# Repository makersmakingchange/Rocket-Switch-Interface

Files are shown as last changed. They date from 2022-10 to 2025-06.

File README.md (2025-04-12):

# Rocket Switch Interface
The Rocket Switch Interface is a switch interface device which enables users to operate their computer or smartphone devices using assistive switches. The Rocket Switch Interface supports up to two 3.5 mm assistive switches as input.

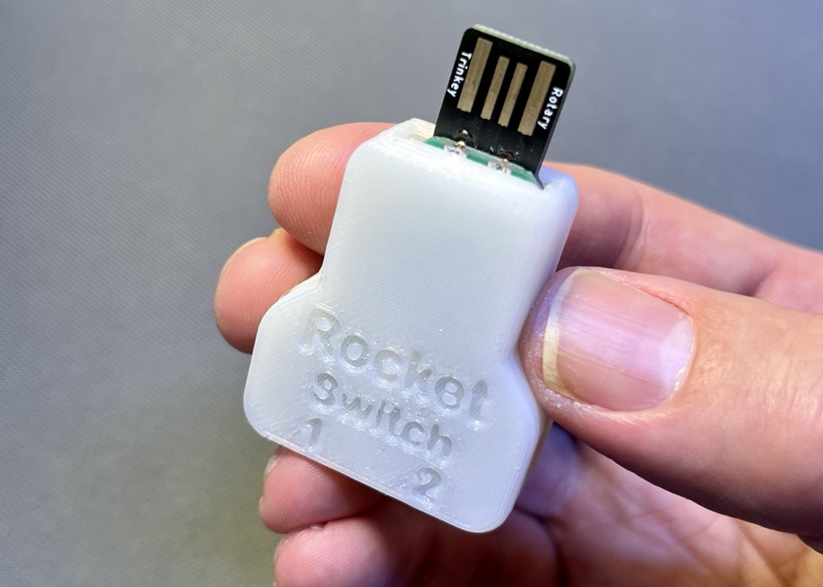
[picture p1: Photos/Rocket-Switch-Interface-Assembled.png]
A picture of a 3d printed Rocket Switch Interface


## More info at
- [Makers Making Change Project Page](https://makersmakingchange.com/project/rocket-switch-interface/)

## Usage
Both switches can be used as inputs when short pressed, Switch 1 can be used to change the operation mode when it's pressed and hold for 4 seconds. The device can operate in several modes:

 - Switch Mac Mode: This mode can be used along switch control software available for Windows, Android, iOS, and Mac Operating Systems. Switch 1 outputs the Space key and switch 2 outputs the Enter key.

 - Switch Mode: This mode can be used along switch control software available for Windows, Android, and iOS Operating Systems. Switch 1 outputs the 1 key and switch 2 outputs the 2 key.

 - Mouse Mode: This mode can be used to simulate a mouse button click. Switch 1 performs left mouse click and switch 2 performs right mouse click.

 - Settings Mode: The settings mode allows the user to adjust the reaction time between switch presses. There are 10 levels in total and the default reaction level is set to 9. The minimum reaction time is 50ms ( Level 10 ) and maximum reaction time is 500ms ( Level 1 ). Switch 1 decrements the reaction level by 1 level and switch 2 increments the reaction level by 1 level as well.

## How to Obtain a Rocket Switch Interface

### 1. Do it Yourself (DIY) or Do it Together (DIT)

This is an open-source assistive technology, so anyone is free to build it. All of the files and instructions required to build the device are contained within this repository. Refer to the Maker Checklist below.

### 2. Request a build of this device

If you would like to obtain this device, you may submit a build request through the [MMC Library Page](https://makersmakingchange.com/project/rocket-switch-interface/). The requestor is responsible for the cost of materials and any shipping.

### 3. How to build this device for someone else

If you have the skills and equipment to build this device, and would like to donate your time to create the switch for someone who needs it, visit the [MMC Maker Wanted](https://makersmakingchange.com/maker-wanted/) section.

## Getting Started

### 1. Read the Makers Checklist

The Makers Checklist provides an overview of the steps required to build this device.

### 2. Order the Off-The-Shelf Components

The [Bill of Materials](/Documentation/Rocket_Switch_Interface_BOM.xlsx) lists all of the parts and components required to build the Rocket Switch Interface.

### 3. Print the 3D Printable components

All of the files and individual print files can be in the [/Build_Files/3D_Printing_Files](/Build_Files/3D_Printing/) folder.

### 4. Assemble the Device

Reference the [Assembly Guide](/Documentation/Rocket_Switch_Interface_Assembly_Guide.pdf) for the tools and steps required to build each portion.

## Files
### Documentation
| Document             | Version | Link |
|----------------------|---------|------|
| Design Rationale     | 1.1     | [Rocket Switch Interface Design_Rationale](/Documentation/Rocket_Switch_Interface_Design_Rationale.pdf)     |
| Maker Checklist      | 1.1     | [Rocket Switch Interface Link_Maker_Checklist](/Documentation/Rocket_Switch_Interface_Maker_Checklist.pdf)     |
| Bill of Materials    | 1.1     | [Rocket Switch Interface Link_Bill_of_Materials](/Documentation/Rocket_Switch_Interface_BOM.xlsx)     |
| 3D Printing Guide    | 1.1     | [Rocket Switch Interface Link_3D_Printing_Guide](/Documentation/Rocket_Switch_Interface_3D_Printing_Guide.pdf)     |
| Assembly Guide       | 1.1     | [Rocket Switch Interface Link_Assembly_Guide](/Documentation/Rocket_Switch_Interface_Assembly_Guide.pdf)     |
| User Guide           | 1.1     | [Rocket Switch Interface Link_User_Guide](/Documentation/Rocket_Switch_Interface_User_Guide.pdf)    |
| Changelog            | 1.1     | [Rocket Switch Interface Link_Changelog](/Documentation/Rocket_Switch_Interface_Changelog.pdf)     |

### Design Files
 - [CAD Files](/Design_Files)

### Build Files
 - [3D Printing Files](/Build_Files/3D_Printing_Files)

## Attribution
Designers:
 - Milad Hajihassan, Makers Making Change

Contributors:
 - Derrick Andrews, Makers Making Change

## License
Everything needed or used to design, make, test, or prepare the Rocket Switch Interface Link is licensed under the CERN 2.0 Weakly Reciprocal license <https://ohwr.org/project/cernohl/wikis/Documents/CERN-OHL-version-2> (CERN-OHL-W) . 

Accompanying material such as instruction manuals, videos, and other copyrightable works that are useful but not necessary to design, make, test, or prepare the Rocket Switch Interface are published under a Creative Commons Attribution-ShareAlike 4.0 license https://creativecommons.org/licenses/by-sa/4.0/ (CC BY-SA 4.0).

----

<!-- ABOUT MMC START -->
## About Makers Making Change
[Makers Making Change Logo](https://www.makersmakingchange.com/)

Makers Making Change is a program of [Neil Squire](https://www.neilsquire.ca/), a Canadian non-profit that uses technology, knowledge, and passion to empower people with disabilities.

Makers Making Change leverages the capacity of community based Makers, Disability Professionals and Volunteers to develop and deliver affordable Open Source Assistive Technologies.

 - Website: [www.MakersMakingChange.com](https://www.makersmakingchange.com/)
 - GitHub: [makersmakingchange](https://github.com/makersmakingchange)
 - Bluesky: [@makersmakingchange.bsky.social](https://bsky.app/profile/makersmakingchange.bsky.social)
 - Instagram: [@makersmakingchange](https://www.instagram.com/makersmakingchange)
 - Facebook: [makersmakechange](https://www.facebook.com/makersmakechange)
 - LinkedIn: [Neil Squire Society](https://www.linkedin.com/company/neil-squire-society/)
 - Thingiverse: [makersmakingchange](https://www.thingiverse.com/makersmakingchange/about)
 - Printables: [MakersMakingChange](https://www.printables.com/@MakersMakingChange)

### Contact Us
For technical questions, to get involved, or to share your experience we encourage you to [visit our website](https://www.makersmakingchange.com/) or [contact us](https://www.makersmakingchange.com/s/contact).
<!-- ABOUT MMC END -->

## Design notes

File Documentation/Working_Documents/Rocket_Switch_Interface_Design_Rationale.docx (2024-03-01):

# Introduction

The goal is to create a low-cost switch interface that can be alternative to commercial options. The device needs be able to perform the main functions that is offered in alternative devices.

# Research

Commercial Alternatives

Device | Company | Inputs | Information | Cost ($US)
Swifty (https://orin.com/access/swifty/) | Origin Instruments | - 2 - Stereo Jack (Requires splitter) | - Splitter is sold separately: $10 - USB Extension: $10 | $99
Tapio (https://www.orin.com/access/tapio/) | Origin Instruments | - 2 - Stereo Jack (Requires splitter) | - iPad and iPhone Switch Interface | $120
Tecla Shield (https://www.iaccessibility.com/accessories/switches/index.cgi/product?ID=41) | Tecla | - 2 mono jacks + 4 way Joystick d-pad | - Discontinued? - 9-pin DB connection for joysticks
Hitch 2 (https://www.especialneeds.com/shop/assistive-technology/switches/switch-interfaces/hitch-2.html) | Ablenet | - 4 | - Ability to program one to four keystrokes of your choice - 9-pin DB connection for joysticks | $120
JoyCable (https://thinksmartbox.com/product/joycable/) | Thinksmartbox | - 2 | - Up to 2 switches (https://thinksmartbox.com/wp-content/uploads/2016/07/JoyCable-manual-July-2016-web-2.pdf) | £99.00 or $118
Crick USB Switch Box (https://www.cricksoft.com/us/crick-usb-switch-box) | Crick Software Inc. | - 4 | - Works on Windows and Mac computers - Crick Software application | $160

DIY Alternatives

Device | Creator | Inputs | Information | Cost ($US)
Enabled Controller Mini (https://makersmakingchange.com/project/enabled-controller-mini/) | Milador | - 4 input jacks and 2-axis analog input | - Morse code mode - Morse mouse mode - Gaming firmware | $40
ATMakers KeySwitch (https://makersmakingchange.com/project/keyswitch/) | ATMakers | - 5 | - Low memory issue with the selected MCU - Gaming firmware | $40
FAIO Multiplexer (https://makersmakingchange.com/project/faio-multiplexer/) | Milador | - 4 | - Morse code mode - Morse mouse mode - Gaming firmware | $55

# Requirements

## Goals

ID | Description
G01 | Cost Effective (Low cost comparing to alternative options)
G02 | Easy to use
G03 | Easy to assemble
G04 | Minimal size

## Functional Requirements

ID | Description
F01 | The device shall have one or more input channels.
F02 | The device shall send output data via USB HID to the host device.
F03 | The device shall be compatible with switch control software.
F04 | The device switch shall incorporate minimal input protection.
F05 | The device latency shall not exceed 50 milliseconds.
F06 | The device shall support visual feedback for user interactions.
F07 | The device shall not consume more than 20 mA of current from the USB port.
F08 | The device shall be able to perform Mouse button, joystick button and keyboard emulation.
F09 | The device shall weigh less than 25 grams.
F10 | The device shall be smaller than 50mm x 40mm x 20mm.

## Non-functional Requirement

ID | Description
NF01 | Shall look professional with tight tolerance on case size.
NF02 | Input ports should be legibly labelled for easy identification

## Constraints

ID | Description
C01 | Shall be able to be built as a single unit for ≤ $40 CAD
C02 | Shall be easily manufacturable by a moderately skilled maker

# Ideation

The initial idea was to add a custom PCB to an existing, small-sized commercially available microcontroller board.

There are a few other ways this could be accomplished:

- Using components with a proto board and breadboard-friendly 3.5 mm jacks
- Using components in a 3D printed jig / 3d printed PCB
- Using panel mount switch jacks mounted in a 3d printed enclosure

## Production Options

Simple maker manufacturing

a. Custom PCB
b. 3D printed case
c. Thru-hole soldering
d. Programming through open-source software

# Conceptual Design

## Components

### Dev Board/MCU

The TRINKEY board is a great low-cost option to design the switch interface based of it, as it offers the basic requirement for creation of a switch interface. Trinkey offer one to three GPIO’s and a built-in RGB LED in a small footprint (USB Flash Stick size).

The Trinkey is offered in following versions:

1. Adafruit NeoKey Trinkey (https://www.adafruit.com/product/5020)
      - Digikey Link: https://www.digikey.ca/en/products/detail/adafruit-industries-llc/5020/14307382
      - Cost: $10 CAD
      - Pros:
        - USB NeoPixel Mechanical Key Switch
        - LED Visible from top and bottom
        - One Touch pad
        - Factory code is compatible with Switch control on Android
      - Cons:
        - One GPIO
        - No exposed ground pad (Needs to use pull down)
2. Adafruit Rotary Trinkey (https://www.adafruit.com/product/4964)
      - DigiKey Link: https://www.digikey.ca/en/products/detail/adafruit-industries-llc/4964/14307384
      - Cost: $10
      - Pros:
        - 2 Analog pins and 1 digital pin exposed which can be used as three GPIO’s
        - One Touch pad
        - Power and ground pads exposed
      - Cons:
        - Factory code is not compatible with switch control software
        - LED Visible from bottom side
3. Adafruit Proximity Trinkey (https://www.adafruit.com/product/5022)
      - Digikey Link: https://www.digikey.ca/en/products/detail/adafruit-industries-llc/5022/15222465
      - Cost: $14 CAD
      - Pros:
        - Two Touch pads
        - Two RGB LEDs on top side
      - Cons:
        - Factory code is not compatible with switch control software
        - No Exposed GPIO’s
        - No exposed power and ground pad

This is not a suitable option because there are no solder pads readily accessible to connect a switch easily.

Both the Adafruit NeoKey Trinkey and the Adafruit Rotary Trinkey could be used to create a switch interface. The Adafruit Rotary Trinkey was selected for the following reasons:

1. Ability to use 2 switches
2. Ground pad is exposed.
3. The rotary switch has thru hole connections that make it easier to connect the switch jacks.

### 3.5 mm Input Jack Options

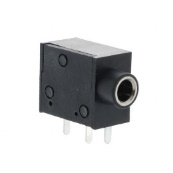
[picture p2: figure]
SJ1-3533NG
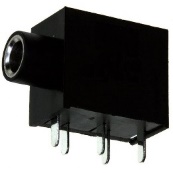
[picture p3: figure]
SJ1-3535NG
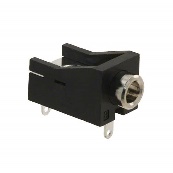
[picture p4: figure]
MJ-3536N
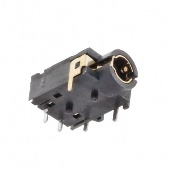
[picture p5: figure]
SJ-43514
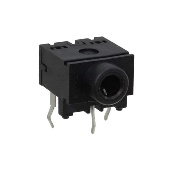
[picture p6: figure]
STX-3120-3B

3.5 mm Jack | SJ1-3533NG | SJ1-3535NG | MJ-3536N | SJ-43514 | STX-3120-3B
Type | Stereo (3 Conductor, TRS) | Stereo (3 Conductor, TRS) | Mono | Stereo (4 Conductor, TRRS) | Stereo (3 Conductor, TRS)
Cost (CAD$) | 1.9 to 1.92 | 1.93 to 1.96 | 1.37 to 1.39 | 1.45 to 1.47 | 1.15 to 1.16
Availability | 689,251 from Digikey, 21,251 from Mouser | 109,033 from Digikey, 5,468 from Mouser | 22,746 from Digikey, 8,534 from Mouser | 28,000 from Digikey, 27,750 from Mouser | 4,467 from Digikey, 5,220 from Mouser
Manufacturer | CUI Devices | CUI Devices | CUI Devices | CUI Devices | Kycon, Inc.
Dimensions | 14(+4) mm x 8.2mm x 12.3mm | 14(+4) mm x 8.2mm x 12.3mm | 15.8(+3) mm x 10mm x 10mm | 11(+3) mm x 4.9mm x 5mm | 10.5(+3.5) mm x 12mm x 10mm
Number of Sets | 1 | 1 | 1 | 1 | 1
Number of Positions | 3 Conductors, 3 Contacts | 3 Conductors, 5 Contacts | 2 Conductors, 3 Contacts | 4 Conductors, 4 Contacts | 3 Conductors, 3 Contacts
Voltage - Rated | 12VDC | 16VDC | 12VDC | 12VDC | N/A
Current Rating | 1A | 1A | 1A | 1A | N/A
Internal Switch | None | 2 Switches | Single Switch | None | None
ProtoBoard Friendly | No | No | No | No | Yes

Trinkey doesn’t provide enough pins to support jack internal switch (touch pad may not be a reliable method to provide additional input)

SJ-43514 is a reliable and low-cost option.

### Hardware pullup

Hardware pullup can be added as an optional feature

### Mounting Hole

A single M3 mounting hole to provide additional support for the enclosure.

## Concepts

### Concept 1: Mono

- Adafruit NeoKey Trinkey (https://www.adafruit.com/product/5020)
- One switch input through pull-down resistor
- Factory code can be used
- Total cost without PCB: $11.36
- Adafruit NeoKey Trinkey x 1: $9.73
- SJ-43514 3.5mm Jack Stereo x 1: $1.48
- 4.7 kΩ 1/4W Through Hole Resistor x 1: $0.15

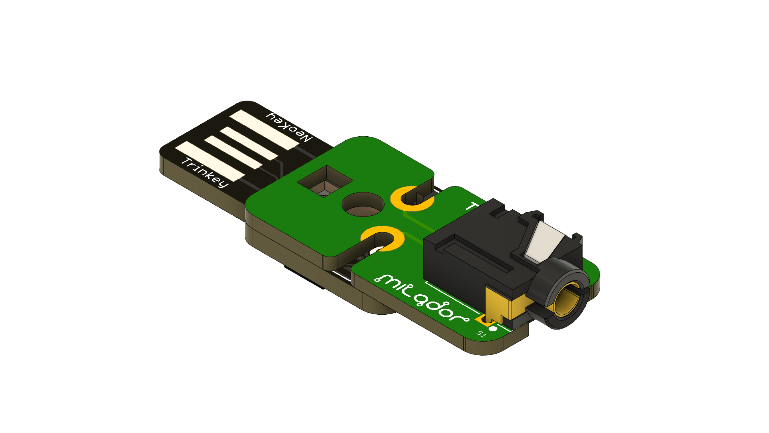
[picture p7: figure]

### Concept 2: Dual version 1

- Adafruit Rotary Trinkey (https://www.adafruit.com/product/4964)
- Two switch inputs through software/hardware pull-up resistor
- Low-cost option
- Total cost without PCB: $12.99
1) Adafruit Rotary Trinkey x 1: $9.73
2) SJ-43514 3.5mm Jack Stereo x 2: $1.48
3) 4.7 kΩ 1/4W Through Hole Resistor x 2: $0.15

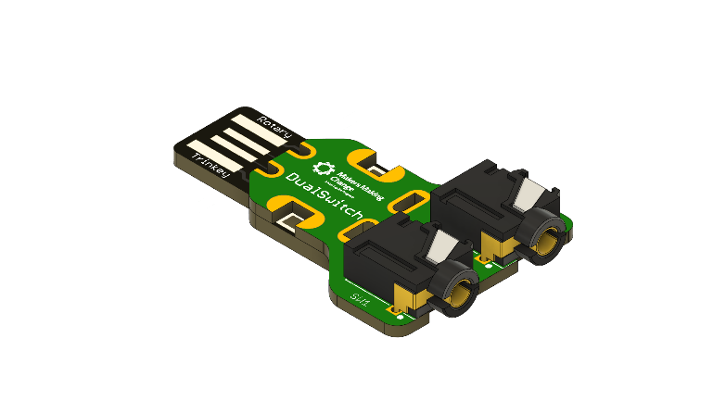
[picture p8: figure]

### Concept 3: Dual Version 2

- Adafruit Rotary Trinkey (https://www.adafruit.com/product/4964)
- Two vertical switch inputs (Jack with 2 sets) through software pull-down resistor
- Total cost without PCB: $14.47
4) Adafruit Rotary Trinkey x 1: $9.73
5) SJ-43514 3.5mm Jack Stereo x 1: $4.44
6) 4.7 kΩ 1/4W Through Hole Resistor x 2: $0.15

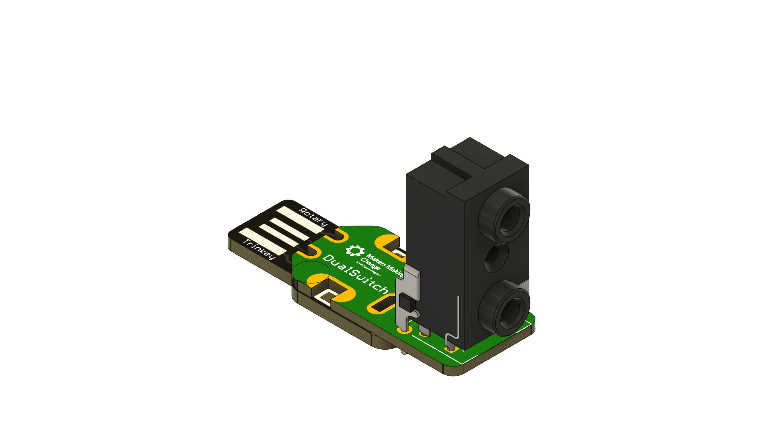
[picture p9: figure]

### Concept 4: Dual Version 3

- Adafruit NeoKey Trinkey (https://www.adafruit.com/product/5020)
- Two switch inputs through software/hardware pull-up resistor
- Total cost without PCB: $12.99
1) Adafruit NeoKey Trinkey x 1: $9.73
2) SJ-43514 3.5mm Jack Stereo x 2: $1.48
3) 4.7 kΩ 1/4W Through Hole Resistor x 2: $0.15

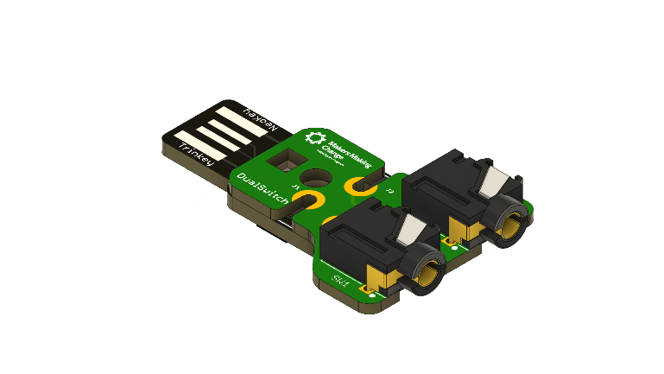
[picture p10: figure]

### Concept 5: Triple

- Adafruit Rotary Trinkey (https://www.adafruit.com/product/4964)
- Three vertical switch inputs (Jack with 3 sets) through software pull-up resistor
- Total cost without PCB: $14.85
4) Adafruit NeoKey Trinkey x 1: $9.73
5) SJ-43514 3.5mm Jack Stereo x 1: $4.67
6) 4.7 kΩs 1/4W Through Hole Resistor x 3: $0.15

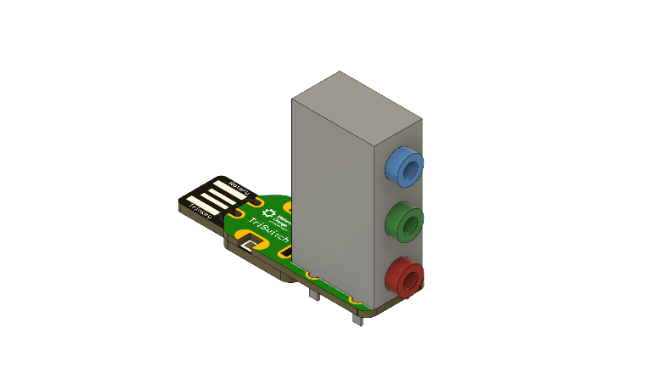
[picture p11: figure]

### Concept 6: Breadboard

- Adafruit Rotary Trinkey (https://www.adafruit.com/product/4964)
- SparkFun ProtoBoard
- Two breadboard friendly 3.5mm switch inputs through software pull-up resistor
- Total cost: $16.13
1) Adafruit NeoKey Trinkey x 1: $9.73
2) STX-3120-3B 3.5mm Jack Stereo x 2: $1.16
3) 4.7 kΩs 1/4W Through Hole Resistor x 2: $0.15
4) SparkFun ProtoBoard - Square 1" Single Sided x 1: $2.73
5) Hook-Up Wire x 1: $1.05

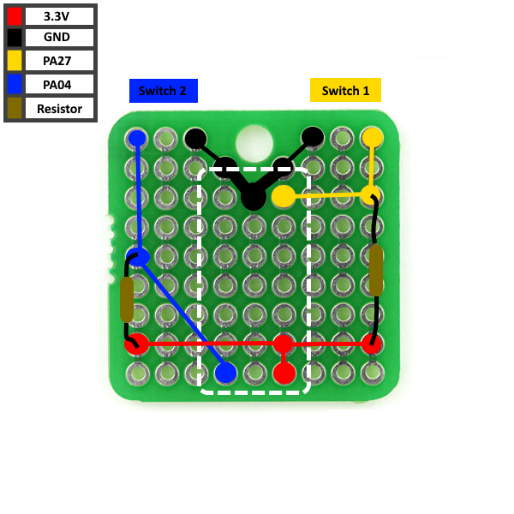
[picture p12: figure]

### Protoboard / Breadboard

Item | Dimension | Availability | Cost $CAD | Link
Sparkfun - Square 1" Single Sided | 2.54mm x 2.54mm ( 9 by 9 0.1 standard spacing) | 2000 units available from Digikey and 388 from Mouser | $2.42 to $3.99 | Digikey (https://www.digikey.ca/en/products/detail/sparkfun-electronics/PRT-08808/7387401) Mouser (https://www.mouser.ca/ProductDetail/SparkFun/PRT-08808?qs=WyAARYrbSnYE9naQ%252BrkzGQ%3D%3D&mgh=1) Sparkfun (https://www.sparkfun.com/products/8808) elmwoodelectronics (https://elmwoodelectronics.ca/products/8808)
ELEGOO Double Sided PCB Board | 20mm x 80mm to 90mm x 150mm | Amazon and AliExpress 70mm x 100mm version on Mouser (https://www.mouser.ca/ProductDetail/Seeed-Studio/319030009?qs=SElPoaY2y5JaWFOX29wUwA%3D%3D&mgh=1) | $1.97 to $3.45 Or $0.56 per unit for 32 units | Amazon.ca (https://www.amazon.ca/Veroboard-Stripboard-Prototype-Soldering-Compatible/dp/B072Z7Y19F) Aliexpress (https://www.aliexpress.com/item/1005001621976056.html)
Chip Quik Solder-in breadboard | 44.5mm x 17.8mm | 86 units available from Digikey and 48 from Mouser | $1.5 to $1.62 | Digikey (https://www.digikey.ca/en/products/detail/chip-quik-inc/SBBTH1506-1/5978222) Mouser (https://www.mouser.ca/ProductDetail/Chip-Quik/SBBTH1506-1?qs=gjT6naH6P5K7JrxFPe%252BjSQ%3D%3D)

STX-3120-3B 3.5mm jack would be idea for this concept due to it’s breadboard friendly characteristic.

### Concept 7: 3D Printed

- Adafruit Rotary Trinkey (https://www.adafruit.com/product/4964)
- Total cost: $13.9
1) Adafruit NeoKey Trinkey x 1: $9.73
2) STX-3120-3B 3.5mm Jack Stereo x 2: $1.16
3) 4.7 kΩs 1/4W Through Hole Resistor x 2: $0.15
4) Hook-Up Wire x 1: $1.05
5) Filament Cost: ~ $0.5

## Circuit Board

1. PCB (Dual Concept 1)

Units | 1 | 5 | 10
Minimum order Unit | 5 | 5 | 5
PCB Cost $US | $2 ($2.6 CAD) | $2 ($2.6 CAD) | $2 ($2.6 CAD)
Shipping Cost $US | ~$18 ($23.5 CAD) | ~$18 ($23.5 CAD) | ~$18 ($23.5 CAD)
Component Cost $US | $9.94 ($12.99 CAD) | $49.7 ($64.95 CAD) | $99.4 ($129.9 CAD)
Unit Cost $(US) | $29.91 ($39.09 CAD) | $13.93 ($18.21 CAD) | $11.94 ($15.6 CAD)

2. 3D Printed
  - Unit cost: $10.2 ($13.9 CAD)

## Concept Selection

- Low cost ($10 less than Enabled controller Mini)
- Easy to assemble
- Small footprint
- Individual jacks instead of stereo jack that requires cable adapter.

Concept | Microcontroller | Inputs | Single Unit Cost | Qty 5 Unit Cost | Qty 10 Unit Cost | Size
Mono | Neokey Trinkey | 1 | $37.46 | $16.58 | $13.97 | 32mm x 16.5mm x 11mm (Total: 44.7 x 16.5mm x 11mm)
Dual1 | Rotary Trinkey | 2 | $39.09 | $18.21 | $15.6 | 33.3mm x 29mm x 11mm (Total: 44.6 x 29mm x 11mm)
Dual2 | Rotary Trinkey | 2 | $40.57 | $19.69 | $17.08 | 33.8mm x 16.5mm x 31.7mm (Total: 45.1 x 16.5mm x 31.7mm)
Dual3 | Neokey Trinkey | 2 | $39.09 | $18.21 | $15.6 | 31.8mm x 29mm x 11mm (Total: 44.4 x 29mm x 11mm)
~~Triple~~ | ~~Rotary~~ ~~Trinkey~~ | ~~3~~ | ~~$40.95~~ | ~~$20.07~~ | $17,46 | 41mm x 16.5mm x 42.5mm (Total: 52.3 x 16.5mm x 42.5mm)
Breadboard | Rotary Trinkey | 2 | $16.13 | $16.13 | $16.13 | 10mm x 10mm x 11mm (Total: 21.3 x 10mm x 11mm)
3D Printed | Rotary Trinkey | 2 | $13.9 | $13.9 | $13.9 | N/A

The breadboard concept introduces challenges for makers with assembly process as the solder pads of breadboard pins are not large enough for solder to make connection with solder pads of the Trinkey board. The breadboard concept would require special tools to drill/cut the breadboard. This would make the assembly process complex for most makers and could result in mis assembly of the unit.

The concept selected is to look at offering both the 3D Printed and Dual-Version 1 options, so that a maker can utilize the 3D Printed version for the least expensive option and use a custom PCB when producing quantities of 5 or more.

# Prototyping

- Mono version was fabricated and assembled using PCB.
- The Concept 2: Dual version 1 was fabricated and assembled using PCB.

# Detailed Design

Concept 2: Dual version 1 was selected as the final concept due to the following reasons:

- It offers all the required features including exposed GPIO pads and ground pads
- It’s a more cost-effective option compared to other PCB base concepts
- This concept has a smaller footprint compared to other concepts
- The selected Trinkey board for this concept has additional solder pads which can help with the assembly process of the device.

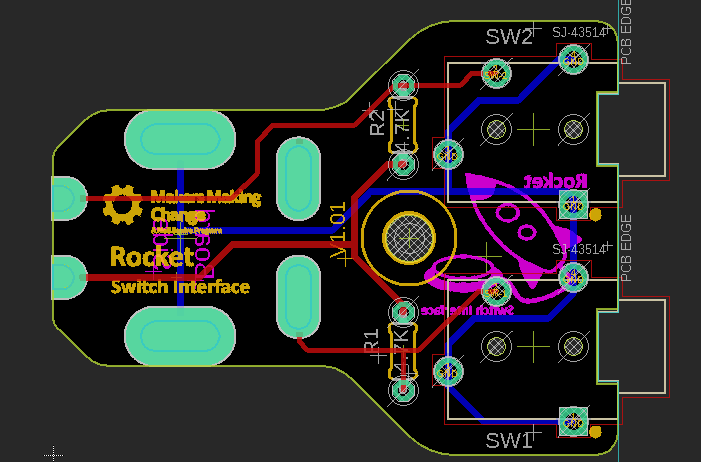
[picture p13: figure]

## Enclosure

<Enclosure Design details>

The enclosure is a snap fit design which includes a top case and bottom case. The two case components are snapped together using four lips added to inner walls of the enclosure. A M3 screw is also inserted through the mounting hole located at the bottom of the enclosure, this is to prevent the PCB to move inside the enclosure. The bottom case includes a cut-out which is used to insert a light pipe.

# Testing

The Mono and Dual versions were successfully tested with Universal Switch accessibility feature of an Android smartphone.

# Opportunities for Improvement

- Create the 3D Printed version for smaller builds of 5 or less
- Improve the software settings and use GUI based settings
- Minimize the dimensions of the case to allow easier connection for USB ports beside

© 2022 by Neil Squire / Makers Making Change. This work is licensed under the CC BY SA 4.0 License: http://creativecommons.org/licenses/by-sa/4.0 Files available at https://makersmakingchange.com/project/rocket-switch-interface/ Page 1 of 1

V1.0 | September 2022 Rocket-Switch-Interface Design Rationale V1.0

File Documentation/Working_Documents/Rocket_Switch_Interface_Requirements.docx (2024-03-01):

# 1. Introduction

The Rocket Switch Interface is intended to be a low-cost switch interface, alternative to commercial options. The device needs to perform the main functions offered by commercial devices.

# 2. Problem Definition

Who

Who will be using the product?

- The Switch Interface is intended to be used primarily by anyone wishing to use adaptive switches and switch control software, to interface with computers or smartphones.

What

What must the device do?

- The source Switch Interface must convert the assistive switch activations, to inputs readable by the host devices (computers or smartphones).
- The Switch Interface must be easy to use.

Where

Where will the device be used?

- The Switch Interface is primarily intended to be used in an assistive switch user’s home, school or office environment.

When

- The Switch Interface is primarily intended to be used during computer or smartphone access/usage sessions.

Why

Why will the device be used?

- The Switch Interface is primarily intended to be used as a low cost, open source switch interface option, alternative to commercial options.

# 3. Functional Properties

## 3.1 Goals

G01 | Cost-effective
G02 | Cost Effective (Low cost comparing to alternative options)
G03 | Easy to use
G04 | Easy to assemble
G05 | Minimal size

## 3.2 Functional Requirements

ID | Description
F01 | The device shall have one or more input channels.
F02 | The device shall send output data via USB HID to the host device.
F03 | The device shall be compatible with switch control software.
F04 | The device switch shall incorporate minimal input protection.
F05 | The device latency shall not exceed 50 milliseconds.
F06 | The device shall support visual feedback for user interactions.
F07 | The device shall not consume more than 20 mA of current from the USB port.
F08 | The device shall be able to perform Mouse button, joystick button and keyboard emulation.
F09 | The device shall weigh less than 25 grams.
F10 | The device shall be smaller than 50mm x 40mm x 20mm.

## 3.3 Non-functional Requirement

ID | Description
NF01 | Shall look professional with tight tolerance on case size.
NF02 | Input ports should be legibly labelled for easy identification

## 3.4 Constraints

ID | Description
C01 | Shall be able to be built as a single unit for ≤ $40 CAD
C02 | Shall be easily manufacturable by a moderately skilled maker

© 2022 by Neil Squire / Makers Making Change. This work is licensed under the CC BY SA 4.0 License: http://creativecommons.org/licenses/by-sa/4.0 Files available at https://makersmakingchange.com/project/rocket-switch-interface/ Page 1 of 1

V1.0 | October 2022 Rocket-Switch-Interface requirements Specifications

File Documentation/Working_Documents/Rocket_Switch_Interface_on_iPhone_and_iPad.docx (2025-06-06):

# Introduction

The Rocket Switch Interface is a small USB switch interface which enables users to operate their digital devices using up to two assistive switches. This guide will go over how to setup the Rocket Switch Interface on an iPhone or iPad using either Switch Control or AssistiveTouch on iOS or iPadOS. For more information on using the Rocket Switch Interface itself, see the User Guide.

# Connecting the Rocket Switch to the iPhone or iPad

## What you need

To use a Rocket Switch Interface on an iPhone or iPad you will need:

- iPhone or iPad
- Charging cable for your mobile device
- USB Adapter with Charging port
- Rocket Switch Interface
- 1 or 2 Assistive Switches

See below for more information on each device.

### iPhone or iPad

These instructions work for iPhones with iOS 13 and newer, or iPads with iPadOS 13 and newer.

### Charging Cable for your iPhone or iPad

This is the cable that you use to charge your iPhone or iPad.

Use this cable to determine if your device has a Lightning charging cable or a USB-C charging cable. Use the table below as a reference:

Lightning Cable | USB-C Cable

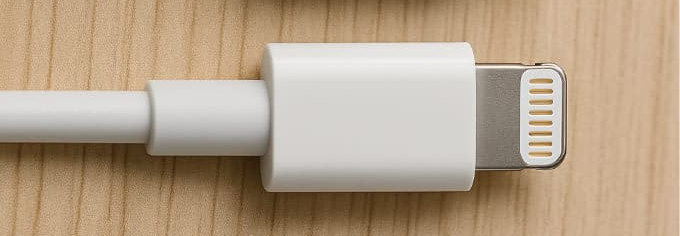
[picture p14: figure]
Close up picture of a Lightning Cable connector.
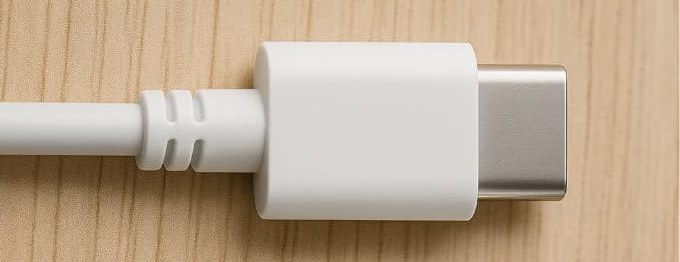
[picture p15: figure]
Close up picture of a USB-C Cable connector.

iPhones 14 and older iPad 9 and older, iPad Mini 4 and older, iPad Air 3 and older, iPad Pro 2 and older | iPhones 15 and newer iPad 10 and newer, iPad Mini 5 and newer, iPad Air 4 and newer, iPad Pro 3 and newer

### USB Adapter with Charging Port

This adapter will depend on whether your device uses a Lightning or USB-C cable (see section above)

Type of Cable | Photo of Adapter | Link to Purchase

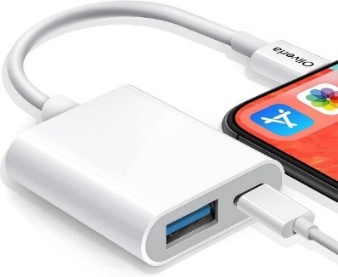
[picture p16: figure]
White USB adapter plugged into an iPhone. Shows a charging cable plugged into it and an empty USB port.

Lightning Cable | | Lightning to USB 3 Camera Adapter - Amazon (https://a.co/d/hhut9rg)

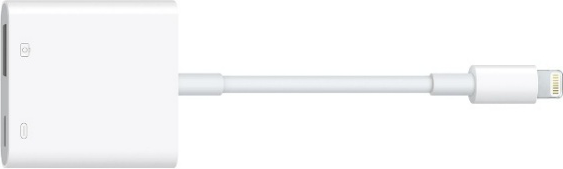
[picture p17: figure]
White Lightning to USB adapter shown laying flat.

| | Lightning to USB 3 Camera Adapter - Apple (https://www.apple.com/ca/shop/product/MX5J3AM/A/lightning-to-usb-3-camera-adapter)

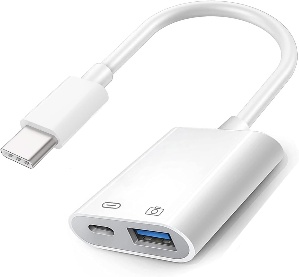
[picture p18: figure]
USB-C to USB adapter with additional power port.

USB-C Cable | | USB-C to USB Camera Adapter - Amazon (https://a.co/d/628FUra)

## Steps

1. Plug charging cable into adapter.
2. Plug Rocket Switch Interface into adapter (ensure it is plugged in in the correct orientation).
3. Plug 1 or 2 assistive switches into the Rocket Switch Interface.
4. Plug the adapter into your iPhone or iPad.

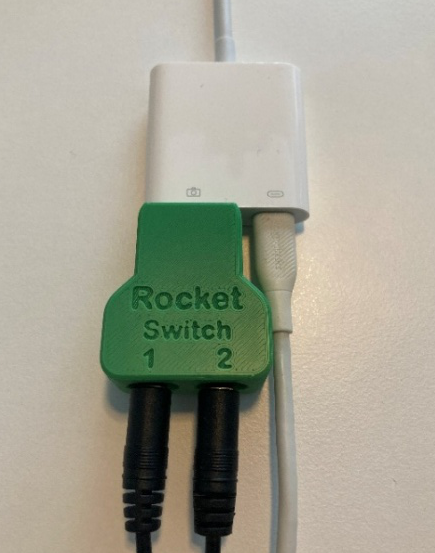
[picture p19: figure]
Rocket Switch Interface plugged into USB adapter, with a charging cable also plugged into it.

Plug into iPhone or iPad

# Setting up the Rocket Switch on the iPhone or iPad

There are two main ways to set up the Rocket Switch Interface on an iPhone or iPad, either through Switch Control or Assistive Touch.

Switch Control uses switch scanning, while Assistive Touch is typically used for cursor control or for buttons to activate shortcuts.

It is recommended to setup your Rocket Switch Interface for Switch Control, unless you are using another device for a cursor/mouse and you want to add mouse clicks (left click and right click) or you want to use the Rocket Switch Interface to activate accessibility controls or shortcuts such as media controls (play/pause, next song, volume, etc).

## Setting up with Switch Control

Using Switch Control with your Rocket Switch Interface can allow your iPhone or iPad to be completely controlled using one or two assistive switches.

To set up Switch Control, first make sure the Rocket Switch Interface is in the correct mode, then follow the steps below, or see this Switch Control Guide from Apple (https://support.apple.com/en-ca/guide/iphone/iph400b2f114/ios).

### Step 1: Rocket Switch Interface Operating Mode

For Switch Control on an Apple device, make sure the Rocket Switch Interface is in Mode 1 – Switch Mac mode, which is indicated by a Teal coloured light on the Rocket Switch Interface. If the LED is not teal, you will need to switch modes by pressing and holding Switch 1 for 4 seconds, cycling through the modes until the LED is teal.

### Step 2: Add Switches and Assign Actions

1. Navigate to Settings > Accessibility > Switch Control > Switches
2. Tap Add New Switch…
3. Select “External” and activate one of the switches plugged into your Rocket Switch Interface.
4. Assign an action to the switch.

This will depend on the number of switches you are using and which switch scanning style you choose. If you don’t know which to assign, try the following:

  - Using 1 Switch: Map to Select Item (this will be compatible with Auto Scanning)
  - Using 2 Switches: Map switch 1 to Select Item and switch 2 to Move To Next Item (this setup will be compatible with Manual Switch Scanning)

Repeat this step if you are using two switches.

### Step 3: Choose a Scanning Style

By default, the cursor automatically moves from one item to the next after a specified duration. If you prefer to move the cursor manually, you can choose a different scanning style.

Go to Settings > Accessibility > Switch Control > Scanning Style, then choose one of the following:

- Auto Scanning: The cursor automatically moves to the next item after a specified duration. This is the default scanning style.
  - If you use Auto Scanning with just one switch, make sure the Select Item action is assigned to the switch.
- Manual Scanning: When you activate your Move to Next Item switch, the cursor moves to the next item.
  - Manual Scanning requires at least two switches. Make sure the Move to Next Item action is assigned to one switch, and the Select Item action is assigned to another switch.
- Single Switch Step Scanning: When you activate the Move to Next Item switch, the cursor moves to the next item; if no action is taken within a specified duration, the current item is automatically selected.
  - This scanning style requires only one switch. Make sure the Move to Next Item action is assigned to the switch.

### Step 4: Fine Tune Switch Control Settings

There are many settings that can be used to adjust the behaviour of Switch Control to suit your needs, to learn more please see this guide: Set up and turn on Switch Control on iPhone (https://support.apple.com/en-ca/guide/iphone/iph400b2f114/ios), and go to Step 4.

If you are using Auto Scanning for example, you may want to adjust the Auto Scanning Time.

### Step 5: Turn on Switch Control

Go to Settings > Accessibility > Switch Control, then turn on Switch Control.

Now you can use your Rocket Switch Interface to control your iPhone or iPad!

## Setting up with AssistiveTouch

Using Assistive Touch with your Rocket Switch Interface is a great way to map assistive switches to specific functions or shortcuts. This may not provide full control of your iPhone or iPad.

### Step 1: Rocket Switch Interface Operating Mode

For Switch Control on an Apple device, make sure the Rocket Switch Interface is in Mode 3 – Mouse mode, which is indicated by a purple coloured light on the Rocket Switch Interface. If the LED is not purple, you will need to switch modes by pressing and holding Switch 1 for 4 seconds, cycling through the modes until the LED is purple.

### Step 2: Turn on Assistive Touch

Go to Accessibility > Touch > AssistiveTouch and then turn on AssistiveTouch.

### Step 3: Add Buttons and Assign Functions

1. Navigate to Accessibility > Touch > AssistiveTouch > Devices.
2. Select your device under “Connected Devices” it will likely be the only one. It may be named “Rotary Trinkey M0”.
3. Press “Customize Additional Buttons”
4. Activate your switch.
5. Assign a function to the switch, there are a long list of available functions, or you can create your own shortcut to activate with your switch (see the next section).
  a. Some examples of functions: Home, App Switcher, Scroll Down, Accessibility Shortcut

### Step 4: (Optional) Create a Custom Shortcut

Custom shortcuts can be created for a large number of actions on Apple devices. To learn more, see the Shortcuts User Guide (https://support.apple.com/en-ca/guide/shortcuts/welcome/ios). Explore the Shortcuts app for different actions you can use in a shortcut, and what might be the most helpful for you.

Some common shortcuts that people might want to map to assistive switches, are media controls such as Play/Pause, or Next Song.

To create a shortcut:

1. Navigate to the Shortcuts app.
2. Go to All Shortcuts, and press the + in the top right corner
3. Press Add Action, and then browse or search for the action you would like, such as searching “Pause” and then selecting “Play/Pause” under the “Media” category.
4. If you want, you can name your shortcut at the top of the window.
5. Press Done in the top right corner.
6. Go back to Step 3 and when assigning a function for the switch, select the name of your new shortcut.

Now you can use your Rocket Switch Interface for AssistiveTouch controls and shortcuts!

© 2025 by Makers Making Change This work is licensed under the CC BY SA 4.0 License: http://creativecommons.org/licenses/by-sa/4.0 Page 1 of 2

JUNE 2025 Rocket Switch Interface Setup Guide for iPhone or iPad

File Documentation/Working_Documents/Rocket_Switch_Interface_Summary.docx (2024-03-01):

# Title

Rocket Switch Interface

## Subtitle

## A cost-effective two input switch interface based on a commercially available Trinkey board.

## Device Specifications

Build Time:

< 1hr

1-4 hr

5-10hr

>10hr

Cost:

$0 - $10

$11 - $25

$26 - $50

$51 - $100

$101 - $250

$250+

Stage:

Skills:

Need:

Electronics, Soldering, 3D Printing, Custom PCB, Software, Engineering

Disability:

Mobility / Physical, Cognitive / Learning

Difficulty:

Intermediate

License:

Attribution-ShareAlike 4.0 International

Usages:

Recreation and Leisure, Computer Access, Communications Aids (AAC)

Type:

Designer:

Milad Hajihassan

## Device Details

### Overview

### The Rocket Switch Interface is a switch interface device which enables users to operate their computer or smartphone devices using adaptive switches. The Rocket Switch Interface supports up to two input 3.5 mm adaptive switches.

### Usage

Both switches can be used as inputs when short pressed, switch 1 can be used to change the operation mode when it’s pressed and hold for 4 seconds. The device can operate in several modes:

• Switch Mode: This mode can be used along switch control software available for Windows and Android Operating Systems. Switch 1 outputs A key and switch 2 outputs B key.

• Switch Mac Mode: This mode can be used along switch control software available for Mac Operating Systems. Switch 1 outputs F1 key and switch 2 outputs F2 key.

• Mouse Mode: This mode can be used to simulate a mouse button click. Switch 1 performs left mouse click and switch 2 performs right mouse click.

• Settings Mode: The settings mode allows the user to adjust the reaction time between switch presses. There are 10 levels in total and the default reaction level is set to 9. The minimum reaction time is 50 ms (Level 10) and maximum reaction time is 500 ms (Level 1). Switch 1 decrements the reaction level by 1 level and switch 2 increments the reaction level by 1 level as well.

### Cost

$45 ($15.16 Components and 3D prints; ~$30 for custom PCB)

### Build Instructions

The Rocket Switch Interface consists of 3D printed parts, electronic components, and custom Arduino program. The Assembly Guide is available at the GitHub repository.

#### Skills Required

- 3D Printing
- Soldering
- Custom PCB
- Microcontroller programming

#### Time Required

3D Printing Time: 49 Minutes

Assembly Time: 20 Minutes

Software Setup Time: 15 Minutes

#### Tools

- Soldering Iron and 60/40 electronics solder
- Needle nose pliers
- Side cutters
- Medium Phillips screwdriver
- Optional clamp or vise to align PCB’s.

#### Components

- 1X Rocket Switch Interface PCB
- 1X Adafruit Rotary Trinkey (i.e., https://www.adafruit.com/product/4964)
- 2X SJ-43514 3.5mm Jack Stereo
- 2X 4.7 kOhms 1/4W Through Hole Resistor
- 1X Light Pipe
- 1X M3 6MM Pan Head Machine Screw Phillip

#### 3D Printing

- 1X Top Case (3D)
- 1X Bottom Case (3D)
- 1X Assembly Jig (3D)

#### Custom PCB

This design utilizes a custom PCB. Five boards (minimum quantity) can be obtained for approximately $30 CAD (shipping included).

#### Programming

A custom Arduino code (Rocket_Switch_Interface.ino) needs to be flashed using Arduino IDE.

### Design

The PCB was designed using Autodesk EAGLE, and the enclosure was designed using Autodesk Fusion 360.

### Attribution

Designed by Makers Making Change

Designer:

Milad Hajihassan, Makers Making Change

Contributors:

Derrick Andrews, Makers Making Change

© 2022 by Neil Squire / Makers Making Change. This work is licensed under the CC BY SA 4.0 License: http://creativecommons.org/licenses/by-sa/4.0 Files available at Neil Squire / Makers Making Change. Page 1 of 2

V1.0 | October 2022 Rocket-Switch-Interface Summary

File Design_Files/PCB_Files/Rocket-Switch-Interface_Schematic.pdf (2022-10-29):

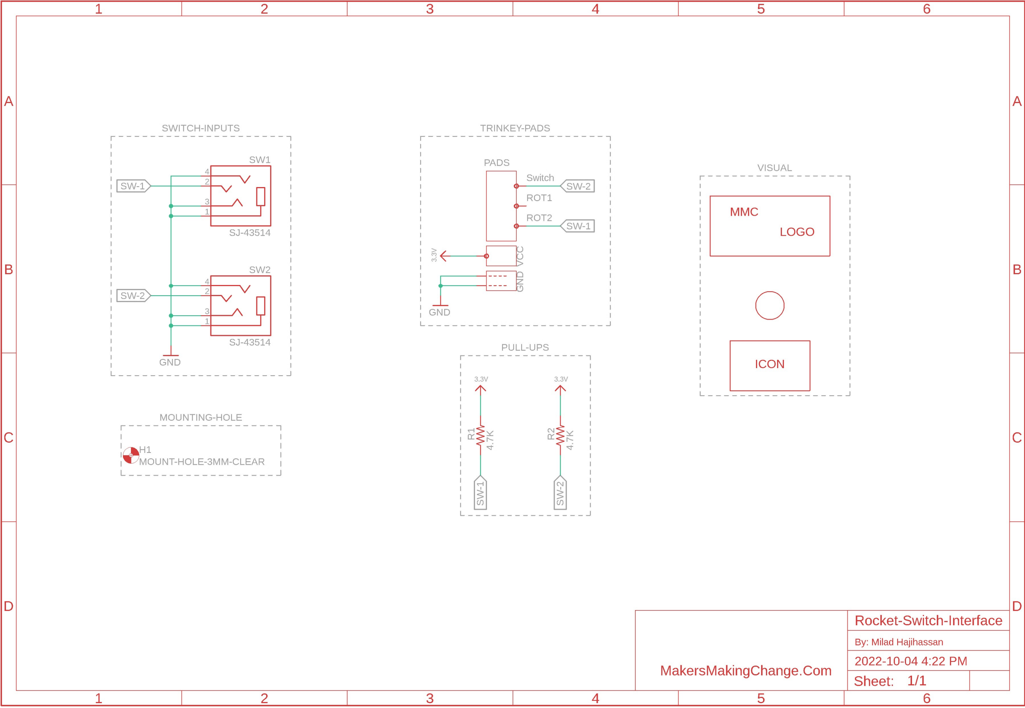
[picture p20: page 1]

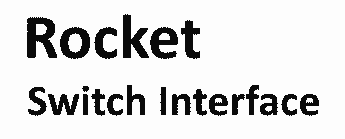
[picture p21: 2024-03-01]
Development/Hardware/PCB/Resources/Rocket_Switch_Interface_Name.bmp

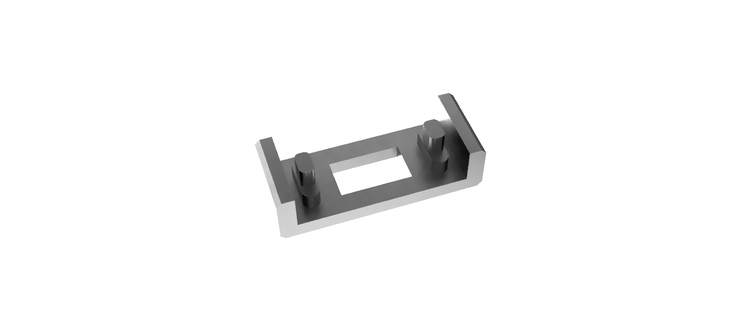
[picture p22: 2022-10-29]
Photos/Rocket-Switch-Interface-Jig.PNG

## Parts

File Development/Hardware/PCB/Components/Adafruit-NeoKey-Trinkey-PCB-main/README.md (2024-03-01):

## Adafruit NeoKey Trinkey PCB

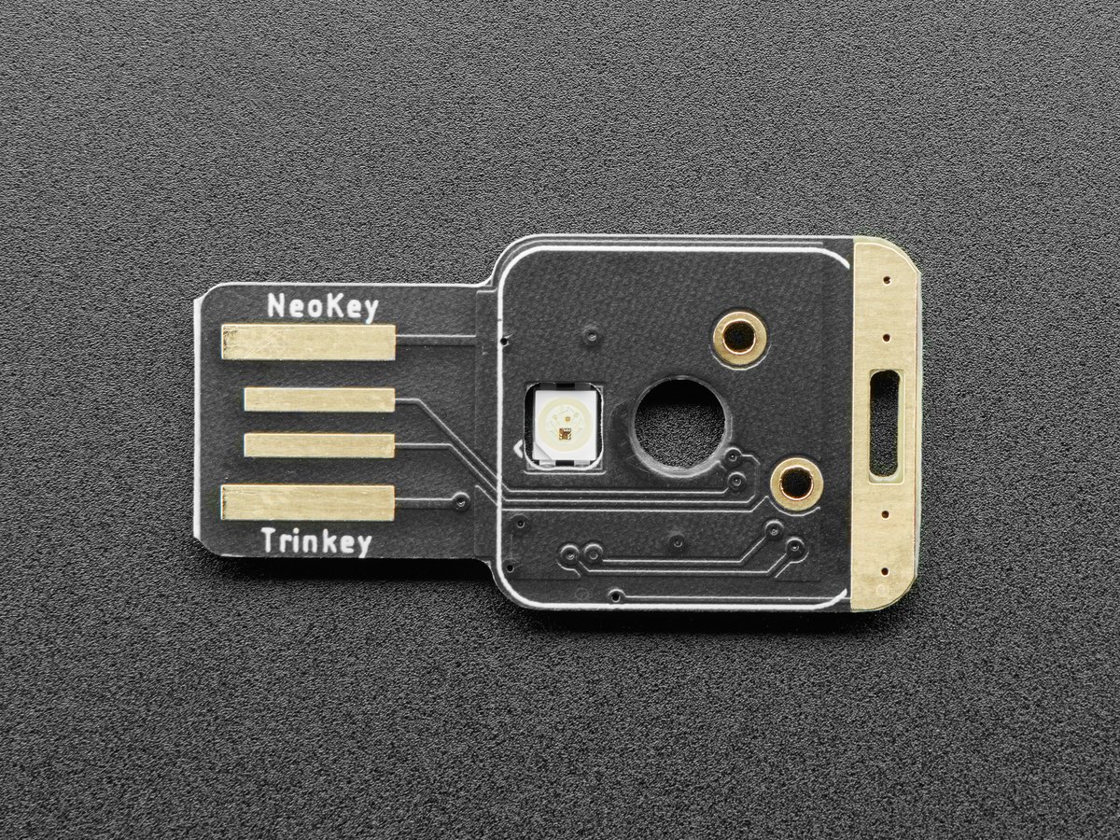
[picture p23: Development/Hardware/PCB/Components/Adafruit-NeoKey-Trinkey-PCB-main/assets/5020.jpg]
<a href="http://www.adafruit.com/products/5020"><br/>
Click here to purchase one from the Adafruit shop</a>

PCB files for the Adafruit NeoKey Trinkey. 

Format is EagleCAD schematic and board layout
* https://www.adafruit.com/product/5020

### Description

It's half USB Key, half Adafruit Trinket, half mechanical keeb...it's NeoKey Trinkey, the circuit board with a Trinket M0 heart, a NeoPixel glow, and a Cherry MX-compatible. We were inspired by single-key macro pads we've seen. So we thought, hey what if we made something like that that plugs right into your computer's USB port, with a fully programmable color NeoPixel? And this is what we came up with!

The PCB is designed to slip into any USB A port on a computer or laptop. There's an ATSAMD21 microcontroller on board with just enough circuitry to keep it happy. One pin of the microcontroller connects to a Cherry MX-compatible switch. Another connects to a NeoPixel LED. The third pin can be used as a capacitive touch input. A reset button lets you enter bootloader mode if necessary. That's it!

The SAMD21 can run CircuitPython or Arduino very nicely - with existing NeoPixel and our FreeTouch libraries for the capacitive touch input. Over the USB connection you can have serial, MIDI or HID connectivity. The NeoKey Trinkey is perfect for simple projects that can use a few user inputs and colorful output. Maybe you'll set it up as a macro-controller, or a password-enterer, or an Escape key for your MacBook.

Please note this board DOES NOT come with a key soldered in - we expect folks to pick their favorite MX-compatible key switch and key cap! Two solder points and you're done.

We think it's just an adorable little board, small and durable and inexpensive enough that it could be a first microcontroller board, or inspiration for advanced developers to make something simple and fun.

* ATSAMD21E18 32-bit Cortex M0+ - 48 MHz 32 bit processor with 256KB Flash and 32 KB RAM
* Native USB supported by every OS - can be used in Arduino or CircuitPython as USB serial console, MIDI, Keyboard/Mouse HID, even a little disk drive for storing Python scripts.
* Can be used with Arduino IDE or CircuitPython
* Single reverse-mount RGB NeoPixel LED
* One Capacitive Touch pad
* Cherry-MX compatible footprint can be used by nearly any mechanical switch. Note we only have a center-nub hole. If your switch has two mini side-nubs they need to be clipped off.
* Reset switch for starting your project code over or entering bootloader mode
* Cute & keychain-friendly!

### License

Adafruit invests time and resources providing this open source design, please support Adafruit and open-source hardware by purchasing products from [Adafruit](https://www.adafruit.com)!

Designed by Limor Fried/Ladyada for Adafruit Industries.

Creative Commons Attribution/Share-Alike, all text above must be included in any redistribution. 
See license.txt for additional details.

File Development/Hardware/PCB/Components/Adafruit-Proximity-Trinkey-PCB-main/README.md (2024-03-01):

## Adafruit Proximity Trinkey PCB

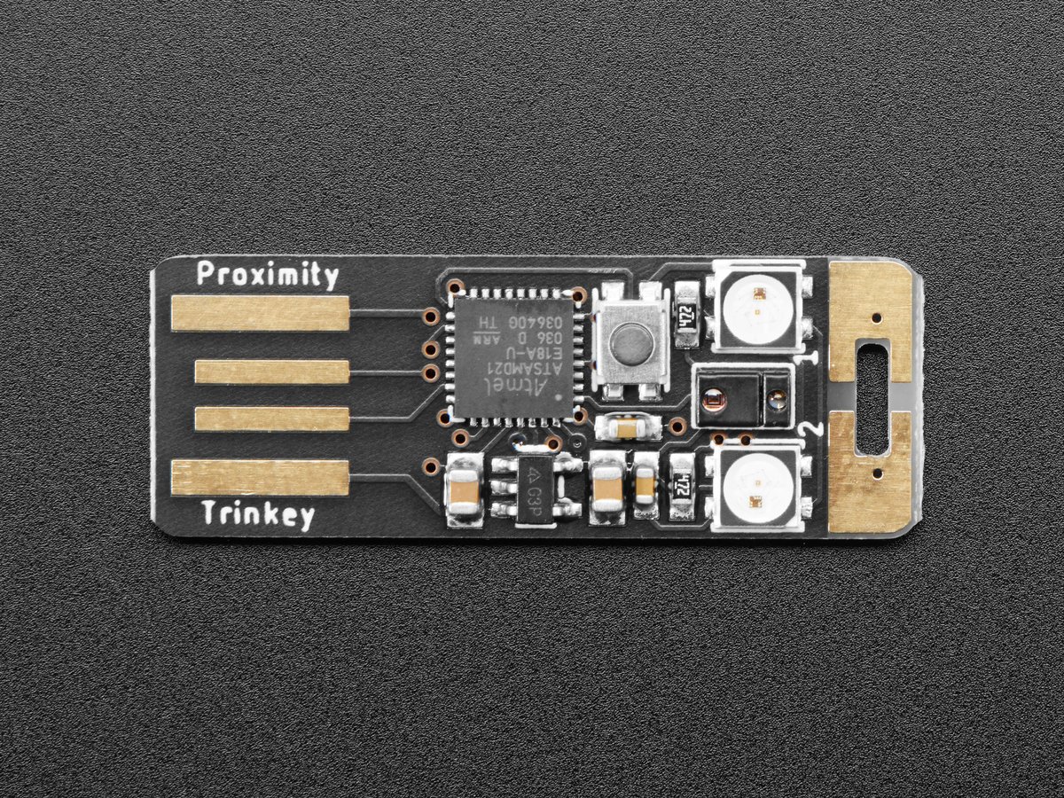
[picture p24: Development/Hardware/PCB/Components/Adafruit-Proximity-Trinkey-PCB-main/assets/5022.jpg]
<a href="http://www.adafruit.com/products/5022"><br/>
Click here to purchase one from the Adafruit shop</a>

PCB files for the Adafruit Proximity Trinkey. 

Format is EagleCAD schematic and board layout
* https://www.adafruit.com/product/5022

### Description

It's half USB Key, half Adafruit Trinket M0, half APDS9960 breakout...it's Proximity Trinkey, the circuit board with a Trinket M0 heart, APDS9960 Proximity, Light, RGB, and Gesture Sensor, and two RGB NeoPixels for a customizable glow. We wanted to make it super-easy to add one of our most popular combination-sensors to any computer with a USB port and this one is ready to go in an instant.

The PCB is designed to slip into any USB A port on a computer or laptop. There's an ATSAMD21 microcontroller on board with just enough circuitry to keep it happy. One pin of the microcontroller connects to the two NeoPixel LEDs. Two other pins are used as capacitive touch inputs on the end - if you look carefully you can see the slotted end has left and right touch pads. A reset button lets you enter bootloader mode if necessary. That's it!

The SAMD21 can run CircuitPython or Arduino very nicely - both have existing APDS9960, NeoPixel and our FreeTouch (capacitive touch) libraries. Over the USB connection, you can have serial, MIDI, or HID connectivity. The Proximity Trinkey is perfect for simple projects that want to use motion, light or color sensing as an input to make fun and intuitive user experiences.

The star of this Trinkey is the APDS9960 from Avago Technologies, which has a few different capabilities thanks to integrated IR LED, photodiodes, and RGB sensing:

* Proximity sensing up to about 6" away by bouncing IR light off an object
* RGB color sensing can detect color when light refects off of an object - good for bright colorful items like LEGO bricks
* Ambient light sensing - how dark or bright is it in the room?
* Basic gesture sensing using 4 cardinal locations of photodiodes - this sensor is a little tough to use but it does work with practice
* Configurable interrupt pin that can fire when a certain proximity threshold is broken, or when a color sensor breaks a certain threshold.

We think it's just an adorable little board, small and durable and inexpensive enough that it could be a first microcontroller board or inspiration for advanced developers to make something simple and fun.

* ATSAMD21E18 32-bit Cortex M0+ - 48 MHz 32 bit processor with 256KB Flash and 32 KB RAM
* Native USB supported by every OS - can be used in Arduino or CircuitPython as USB serial console, MIDI, Keyboard/Mouse HID, even a little disk drive for storing Python scripts.
* Can be used with Arduino IDE or CircuitPython
* Two RGB NeoPixel LEDs
* Two Capacitive Touchpads
* APDS9960 Light/Color/Proximity/Gesture sensor
* Reset switch for starting your project code over or entering bootloader mode
* Slim and cute, keychain-friendly!

### License

Adafruit invests time and resources providing this open source design, please support Adafruit and open-source hardware by purchasing products from [Adafruit](https://www.adafruit.com)!

Designed by Limor Fried/Ladyada for Adafruit Industries.

Creative Commons Attribution/Share-Alike, all text above must be included in any redistribution. 
See license.txt for additional details.

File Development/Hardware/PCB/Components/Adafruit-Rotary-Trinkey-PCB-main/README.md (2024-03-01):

## Adafruit Rotary Trinkey PCB

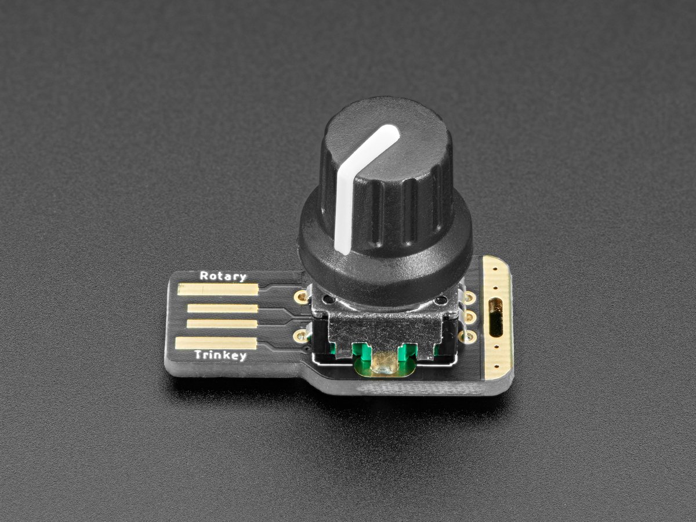
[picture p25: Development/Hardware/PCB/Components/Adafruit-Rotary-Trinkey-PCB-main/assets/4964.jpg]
<a href="http://www.adafruit.com/products/4964"><br/>
Click here to purchase one from the Adafruit shop</a>

PCB files for the Adafruit Rotary Trinkey. 

Format is EagleCAD schematic and board layout
* https://www.adafruit.com/product/4964

### Description

It's half USB Key, half Adafruit Trinket, half rotary encoder...it's Rotary Trinkey, the circuit board with a Trinket M0 heart, a NeoPixel glow, and a rotary encoder body. We were inspired by this project from TodBot where a rotary encoder was soldered onto a QT Py. So we thought, hey what if we made something like that that plugs right into your computer's USB port, with a fully programmable color NeoPixel? And this is what we came up with!

The PCB is designed to slip into any USB A port on a computer or laptop. There's an ATSAMD21 microcontroller on board with just enough circuitry to keep it happy. Three pins of the microcontroller connects to a rotary encoder with built-in push switch. Another connects to a NeoPixel LED. Finally, one pin can be used as a capacitive touch input. A reset button lets you enter bootloader mode if necessary. That's it!

Rotary encoders are soooo much fun! Twist em this way, then twist them that way. Unlike potentiometers, they go all the way around, and often have little detents for tactile feedback. But, if you just want to add one to your computer, you know its a real pain. This board is designed to make it very easy.

The SAMD21 can run CircuitPython or Arduino very nicely - with existing Rotary, NeoPixel and our FreeTouch libraries for the capacitive touch input. Over the USB connection you can have serial, MIDI or HID connectivity. The Rotary Trinkey is perfect for simple projects that use a rotating user input and underlit colorful output. Maybe you'll set it up as a volume knob, scroll wheel, or zoom macro tool - whatever you like!

Please note this board DOES NOT come with a rotary encoder soldered in - we expect folks to pick their favorite rotary encoder and knob! Five solder points and you're done.

We think it's just an adorable little board, small and durable and inexpensive enough that it could be a first microcontroller board or inspiration for advanced developers to make something simple and fun.

* ATSAMD21E18 32-bit Cortex M0+ - 48 MHz 32 bit processor with 256KB Flash and 32 KB RAM
* Native USB supported by every OS - can be used in Arduino or CircuitPython as USB serial console, MIDI, Keyboard/Mouse HID, even a little disk drive for storing Python scripts.
* Can be used with Arduino IDE or CircuitPython
* Single under-lighting RGB NeoPixel LED
* One Capacitive Touch pad
* Standard '5-pin' rotary encoder footprint can be used with any "PEC11" or "PEC12" compatible rotary encoder.
* Cute & keychain-friendly!

### License

Adafruit invests time and resources providing this open source design, please support Adafruit and open-source hardware by purchasing products from [Adafruit](https://www.adafruit.com)!

Designed by Limor Fried/Ladyada for Adafruit Industries.

Creative Commons Attribution/Share-Alike, all text above must be included in any redistribution. 
See license.txt for additional details.

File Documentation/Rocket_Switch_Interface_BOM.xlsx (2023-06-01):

Device: Rocket-Switch-Interface V1.1 |  |  | Total Cost | Total Print time (hr) | Total filament (g)
Version: V1.1 | Date Created: 10/28/2022 |  | $15.32 | 1.02 | 8.65
Commercial Parts:
Part type (Electrical. Mechanical, Sanitization, ect) | Part Name | Part Label | Quantity Needed | Pkg Quantity | Price per package | Price per Unit | Price for qty needed | Link | Alternate Links
Electrical | Adafruit Rotary Trinkey |  | 1 | 1 | $9.73 | $9.73 | $9.73 | https://www.digikey.ca/en/products/detail/adafruit-industries-llc/4964/14307384
Electrical | SJ-43514 3.5mm Jack Stereo | SW1,SW2 | 2 | 1 | $1.48 | $1.48 | $2.96 | https://www.digikey.ca/en/products/detail/cui-devices/SJ-43514/368146
Electrical | 4.7 kOhms 1/4W Through Hole Resistor | R1,R2 | 2 | 1 | $0.15 | $0.15 | $0.30 | https://www.digikey.ca/en/products/detail/stackpole-electronics-inc/CFM14JT4K70/1742213
Electrical | Light Pipe |  | 1 | 1 | $1.70 | $1.70 | $1.70 | https://www.digikey.ca/en/products/detail/dialight/51513030250F/4965201
Electrical | M3 8MM Pan Head Machine Screw Phillip |  | 1 | 1 | $0.41 | $0.41 | $0.41 | https://www.digikey.ca/en/products/detail/w%C3%BCrth-elektronik/97790803111/10056388 | https://www.digikey.ca/en/products/detail/apm-hexseal/RM3X8MM-2701/3712297
3D Printed Parts ESTIMATED PRICING USING 1KG ROLL COST: | $25.00
Part | Description |  | Quantity Needed | TOTAL Mass (g) | Estimated Price | Print Time (Min) | Link
Rocket-Switch-Interface-Bottom-Case | 15% Infill |  | 1 | 4.48 | $0.11 | 29 | https://github.com/makersmakingchange/Rocket-Switch-Interface/tree/main/Build_Files/3D_Print_Files/STL/Rocket-Switch-Interface-Bottom-Case.stl
Rocket-Switch-Interface-Top-Case | 15% Infill |  | 1 | 3.64 | $0.09 | 26 | https://github.com/makersmakingchange/Rocket-Switch-Interface/tree/main/Build_Files/3D_Print_Files/STL/Rocket-Switch-Interface-Top-Case.stl
Rocket-Switch-Interface-Jig | 15% Infill |  | 1 | 0.53 | $0.01 | 6 | https://github.com/makersmakingchange/Rocket-Switch-Interface/tree/main/Build_Files/3D_Print_Files/STL/Rocket-Switch-Interface-Jig.stl
 |  |  |  |  | $0.00
 |  |  |  |  | $0.00
 |  |  |  | Total Print Cost: | $0.22
Tools for Assembly
Soldering iron
Alternatives (if there are other sources for some parts link them below)
Part and description | Link

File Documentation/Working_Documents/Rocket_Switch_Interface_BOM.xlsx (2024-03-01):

Rocket Switch Interface |  |  |  |  |  | Total Cost | Unit Cost | Total filament (g) | Total Print time (hr)
Version: V1.0 | Last Updated: 2022-Oct-28 |  |  |  |  | $21.34 | $21.34 | 8.87 | 0.82
Commercial Parts
Part Name | Part Type | Part Label | QTY | QTY / PKG | Price per package | Price per Unit | Price for qty needed | Link | Alternate Links
Adafruit Rotary Trinkey | Electrical |  | 1 | 1 | $9.73 | $9.73 | $9.73 | https://www.digikey.ca/en/products/detail/adafruit-industries-llc/4964/14307384
SJ-43514 3.5mm Jack Stereo | Electrical | SW1,SW2 | 2 | 1 | $1.48 | $1.48 | $2.96 | https://www.digikey.ca/en/products/detail/cui-devices/SJ-43514/368146
4.7 kOhms 1/4W Through Hole Resistor | Electrical | R1,R2 | 2 | 1 | $0.15 | $0.15 | $0.30 | https://www.digikey.ca/en/products/detail/stackpole-electronics-inc/CFM14JT4K70/1742213
Light Pipe | Electrical |  | 1 | 1 | $1.70 | $1.70 | $1.70 | https://www.digikey.ca/en/products/detail/dialight/51513030250F/4965201
M3 6MM Pan Head Machine Screw Phillip | Electrical |  | 1 | 1 | $0.43 | $0.43 | $0.43 | https://www.digikey.ca/en/products/detail/w%C3%BCrth-elektronik/97790603111/10056387 | https://www.digikey.ca/en/products/detail/apm-hexseal/RM3X6MM-2701/612968
Custom PCB | Electrical | PCB | 1 | 5 | $30.00 | $6.00 | $6.00
3D Printed Parts ESTIMATED PRICING USING 1KG ROLL COST: | $25.00
Part | Description |  | QTY | TOTAL Mass (g) |  | Print Time (Min) | Estimated Price | Link
Rocket-Switch-Interface-Bottom-Case |  |  | 1 | 4.53 |  | 22 | $0.11 | https://github.com/makersmakingchange/Rocket-Switch-Interface/tree/main/Build_Files/3D_Print_Files/STL/Rocket-Switch-Interface-Bottom-Case.stl
Rocket-Switch-Interface-Top-Case |  |  | 1 | 3.83 |  | 22 | $0.10 | https://github.com/makersmakingchange/Rocket-Switch-Interface/tree/main/Build_Files/3D_Print_Files/STL/Rocket-Switch-Interface-Top-Case.stl
Rocket-Switch-Interface-Jig |  |  | 1 | 0.51 |  | 5 | $0.01 | https://github.com/makersmakingchange/Rocket-Switch-Interface/tree/main/Build_Files/3D_Print_Files/STL/Rocket-Switch-Interface-Jig.stl
 |  |  |  |  |  |  | $0.00
 |  |  |  |  |  |  | $0.00
 |  |  |  |  |  | Total Print Cost: | $0.22
Tools for Assembly
Soldering iron
Screwdriver
Alternatives (if there are other sources for some parts link them below)
Part and description | Link

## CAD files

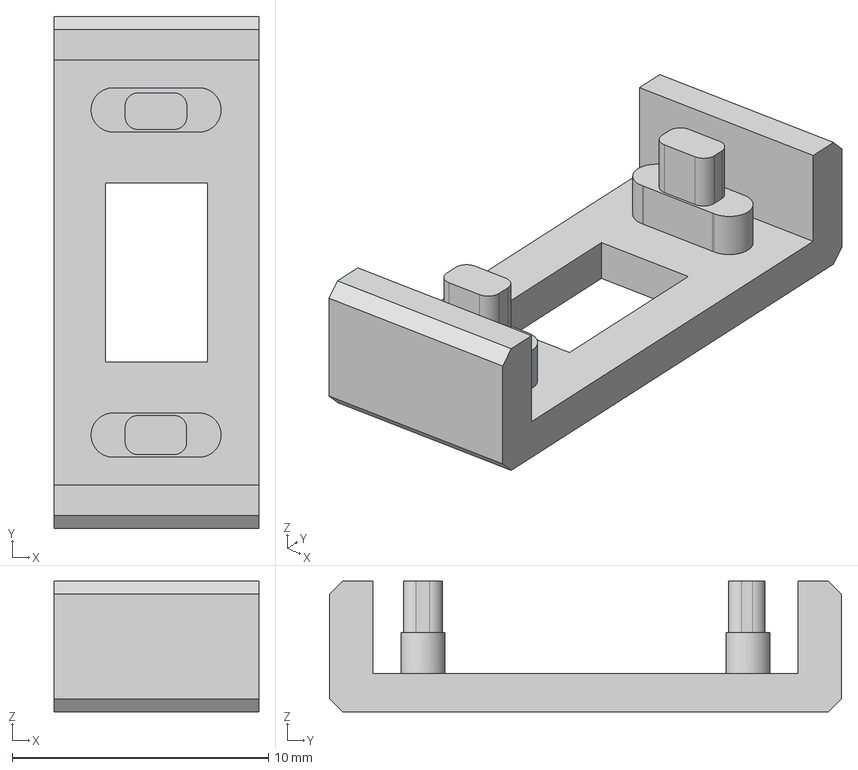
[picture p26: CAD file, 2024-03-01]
Build_Files/3D_Print_Files/STEP/Rocket-Switch-Interface-Jig.step
8.00 x 20.0 x 5.10 mm

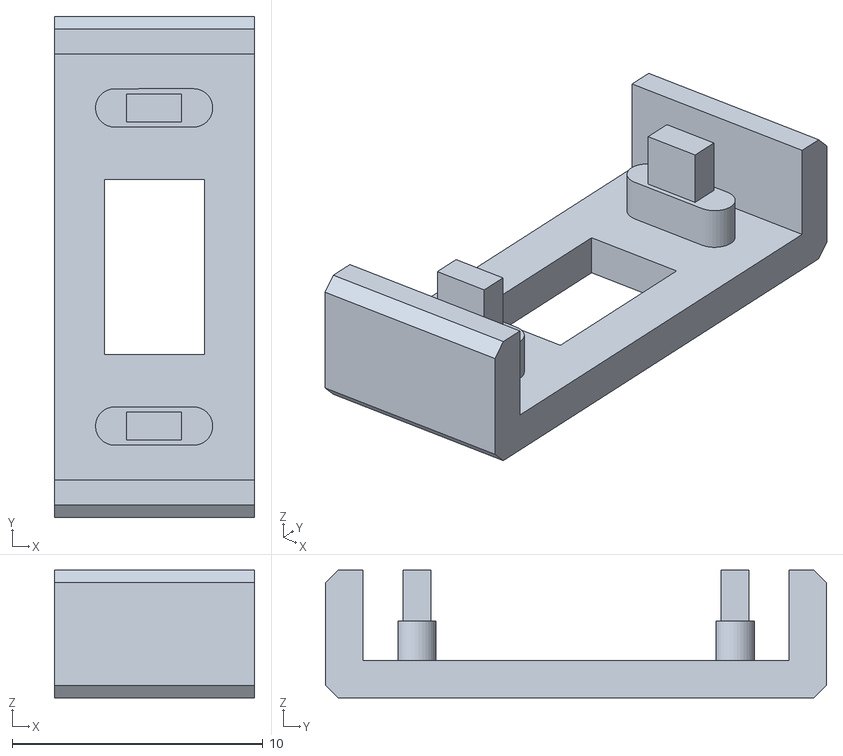
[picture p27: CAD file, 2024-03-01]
Build_Files/3D_Print_Files/STL/Rocket-Switch-Interface-Jig-Tight.stl
8.00 x 20.0 x 5.10

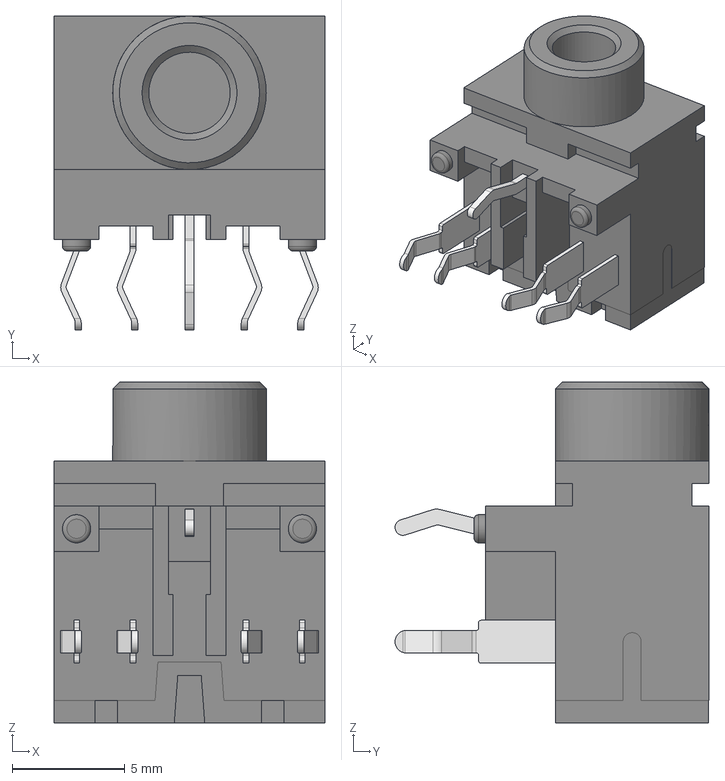
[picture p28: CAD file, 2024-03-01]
Design_Files/CAD/STX-3120-5B.step
12.0 x 13.9 x 15.1 mm

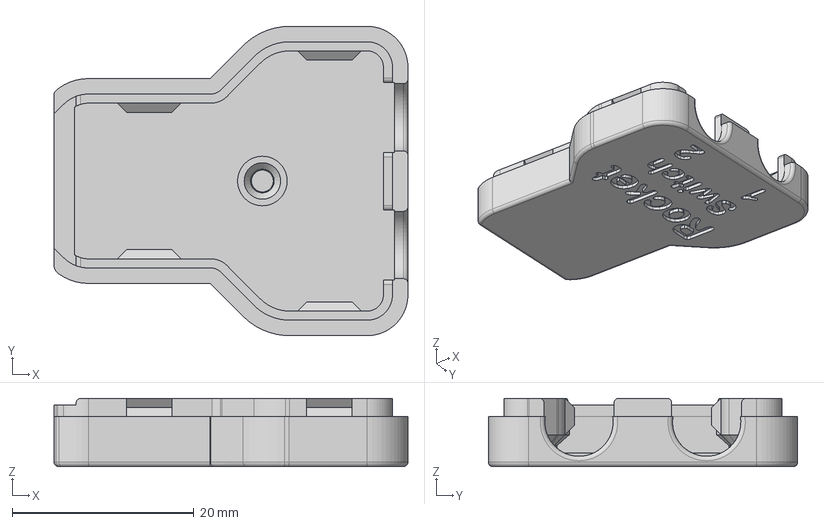
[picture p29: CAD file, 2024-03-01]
Build_Files/3D_Print_Files/STEP/Rocket-Switch-Interface-Top-Case.step
38.9 x 34.0 x 7.50 mm

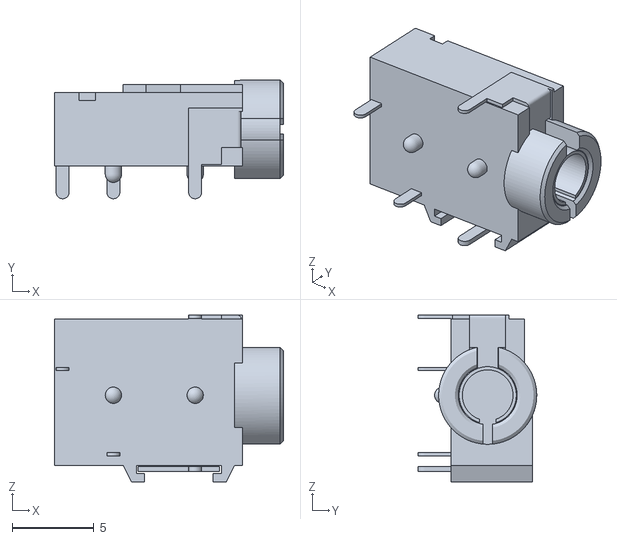
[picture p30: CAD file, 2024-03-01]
Design_Files/CAD/CUI_DEVICES_SJ-43514.stl
14.0 x 7.25 x 10.2

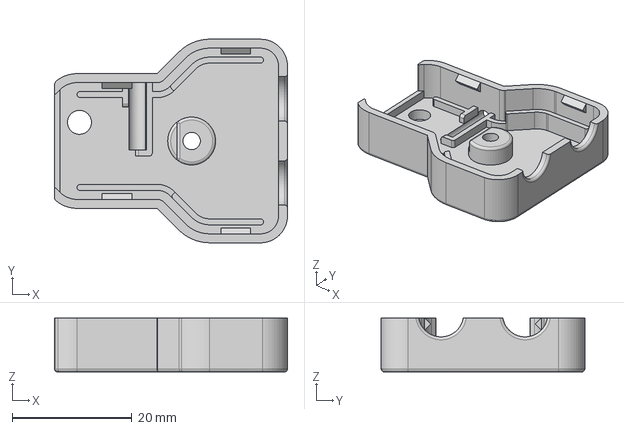
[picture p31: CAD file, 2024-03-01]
Build_Files/3D_Print_Files/STEP/Rocket-Switch-Interface-Bottom-Case.step
38.9 x 34.0 x 9.00 mm

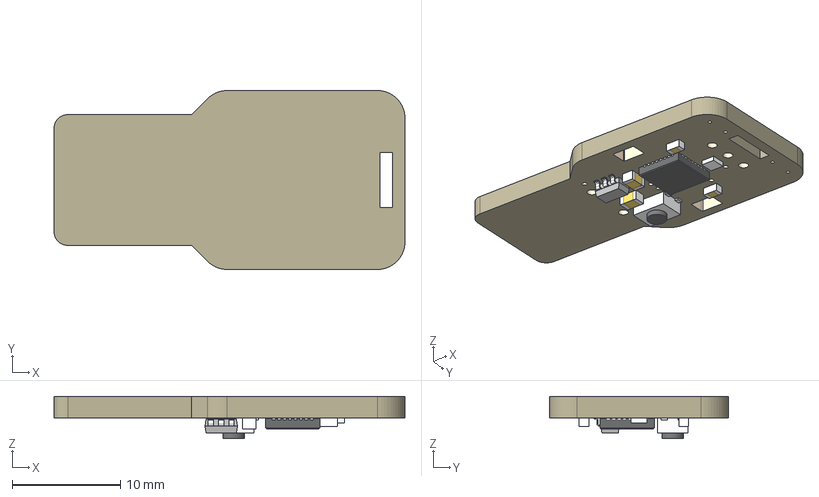
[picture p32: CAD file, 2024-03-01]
Design_Files/CAD/Rotary_Trinkey.step
32.4 x 16.5 x 3.90 mm
Board
10uF x 2
reset
ATSAMD21E
1uF x 2
AP2112K-3.3
WS2812B_SK6805_1515

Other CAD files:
Build_Files/3D_Print_Files/Rocket-Switch-Interface-Bottom-Case.stl
Build_Files/3D_Print_Files/Rocket-Switch-Interface-Jig.stl
Build_Files/3D_Print_Files/Rocket-Switch-Interface-Top-Case.stl
Build_Files/3D_Print_Files/STL/Rocket-Switch-Interface-Bottom-Case.stl
Build_Files/3D_Print_Files/STL/Rocket-Switch-Interface-Jig.stl
Build_Files/3D_Print_Files/STL/Rocket-Switch-Interface-Top-Case.stl
Design_Files/3D_Printing_Files/Rocket-Switch-Interface-Jig.f3z
Design_Files/CAD/Rocket-Switch-Interface-Jig.f3z
Design_Files/CAD/Rotary_Trinkey.stl

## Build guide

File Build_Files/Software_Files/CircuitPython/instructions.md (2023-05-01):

# CircuitPython Installation

To install the CircuitPython Code:

1. Download the following files and folders:

- code.py
- adafruit_hid folder
- adafruit-circuitpython...uf2

2. If you haven't installed CircuitPython to the board previously, double-click the reset button on the board to enter bootloader mode. Drag the .uf2 files into the BOOT drive that appears.

3. Drag and drop the code.py file into the drive.

4. Drag the adafruit_hid folder into the lib folder in the drive.

Note: If you are on a Mac and receive a memory error, you may need to copy the folder using command line instead of dragging and dropping. You will need to:

- Open the Terminal app 
- Navigate to the location of the folder most likely you'll need to enter: </br>
```cd Downloads```

- To copy the entire folder and internal files type: </br>
```cp -rX adafruit-hid /Volumes/CIRCUITPY/lib```

You should now be able to see the adafruit-hid folder inside the lib folder.

That's it! Your Rocket Switch Interface will now send a Tab and Space when your connected switches are pressed.

If you'd like to change the keys being sent: 
1. visit the [Adafruit HID Documentation](https://docs.circuitpython.org/projects/hid/en/latest/_modules/adafruit_hid/keycode.html) for the complete list of keycodes. 

2. Open the ```code.py``` file in a simple text editor or better yet a code editor if you have one installed.
3. Type the desired keycode on line number 25 replacing the TAB or SPACE.
4. Save your file and the updates will automatically be applied.

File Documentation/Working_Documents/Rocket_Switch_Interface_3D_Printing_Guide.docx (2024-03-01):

# 3D Printing Summary

Metrics | V1.0
Total Print Time (min) | 49
Total Number of Components | 3
Typical Total Mass (g) | 8.87
Typical Number of Print Setups | 1

# 3D Printing Settings

Print File Name | Qty | Total Print Time (hr:min) | Mass (g) | Infill (%) | Support (Y/N) | Layer Height/ Nozzle Diameter (mm) | Notes (orientation, special settings, etc.)
Rocket-Switch-Interface-Bottom-Case.stl | 1 | 0:22 | 4.53 | 15 | N | 0.2/0.4
Rocket-Switch-Interface-Top-Case.stl | 1 | 0:22 | 3.83 | 15 | N | 0.2/0.4
Rocket-Switch-Interface-Jig.stl | 1 | 0:05 | 0.51 | 15 | N | 0.2/0.4

# Post-Processing

- Remove any burrs or sharp edges if needed.

# Examples of Quality Prints

Rocket-Switch-Interface-Bottom-Case

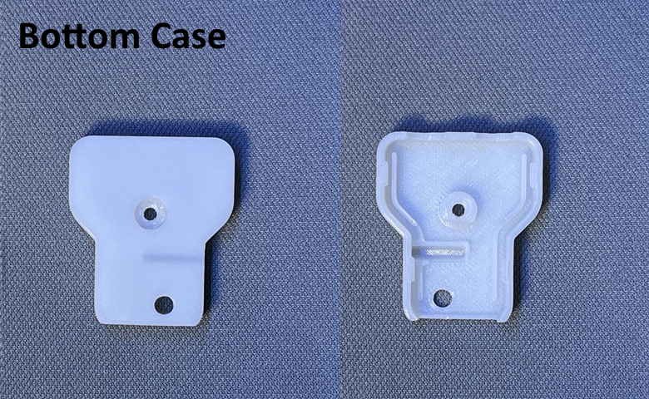
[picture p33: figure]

Rocket-Switch-Interface-Top-Case

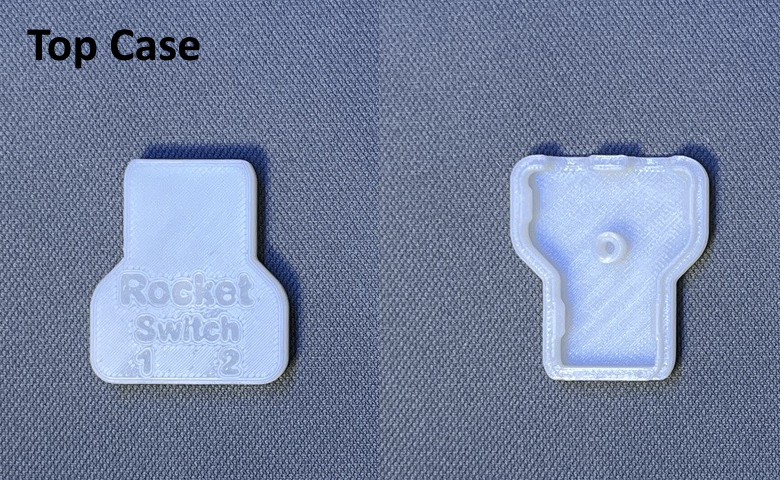
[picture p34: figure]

Rocket-Switch-Interface-Jig

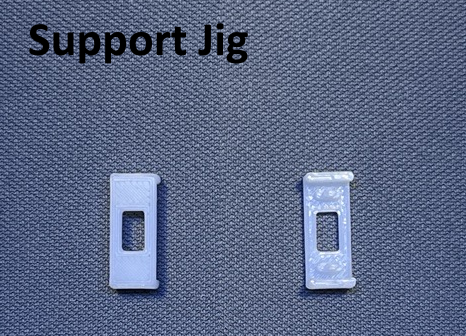
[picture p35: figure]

© 2022 by Neil Squire / Makers Making Change. This work is licensed under the CC BY SA 4.0 License: http://creativecommons.org/licenses/by-sa/4.0 Files available at https://makersmakingchange.com/project/rocket-switch-interface/ Page 1 of 2

V1.0 | October 2022 Rocket-Switch-Interface 3D Printing Guide V1.0

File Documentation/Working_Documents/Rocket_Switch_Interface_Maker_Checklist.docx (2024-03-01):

# Maker To Do List

- Read through the Assembly Guide to become familiar with required components, tools, supplies, and safety gear and overall assembly steps.
- Talk to User about customization options (e.g., color, any special requests, etc.)
- Order custom PCB
- Order hardware components
- Print 3D Printed components
- Gather tools, supplies, and safety equipment.
- Assemble the device
- Test device
- Print “User Quick Guide”

# Items to Give to User

- Assembled, tested device
- “User Quick Guide”

© 2022 by Neil Squire / Makers Making Change. This work is licensed under the CC BY SA 4.0 License: http://creativecommons.org/licenses/by-sa/4.0 Files available at https://makersmakingchange.com/project/rocket-switch-interface/ Page 1 of 1

V1.0 | October 2022 Rocket-Switch-Interface Maker Checklist V1.0

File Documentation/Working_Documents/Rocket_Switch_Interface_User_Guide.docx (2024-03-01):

## Introduction

The Rocket Switch Interface is a USB switch interface device which enables users to operate their computer or smartphone devices using assistive switches. Up to two assistive switches with 3.5 mm connections can be used. When a connected assistive switch is activated, a keystroke or mouse click will be generated depending on the operating mode. The Rocket Switch Interface can operate in three different modes, and has an adjustable reaction time.

## Features

### Switch Inputs

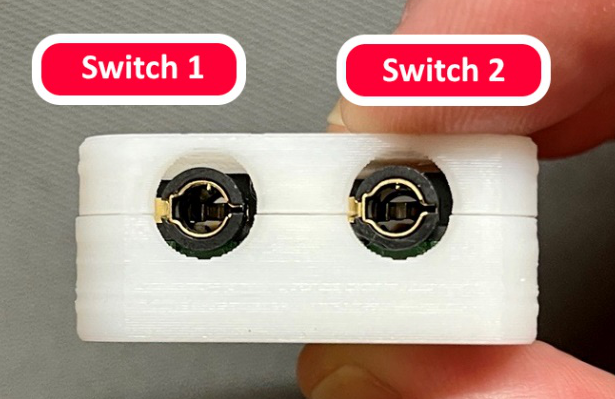
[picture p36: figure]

### Type-A USB Connector

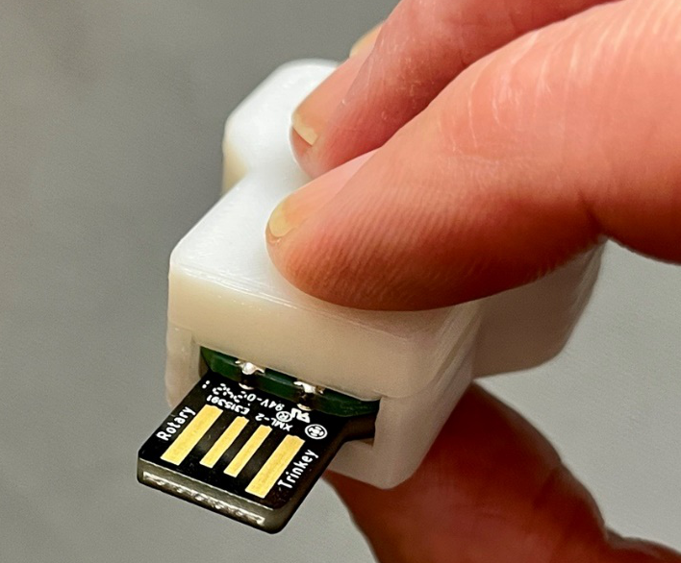
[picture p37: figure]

### LED Indicator

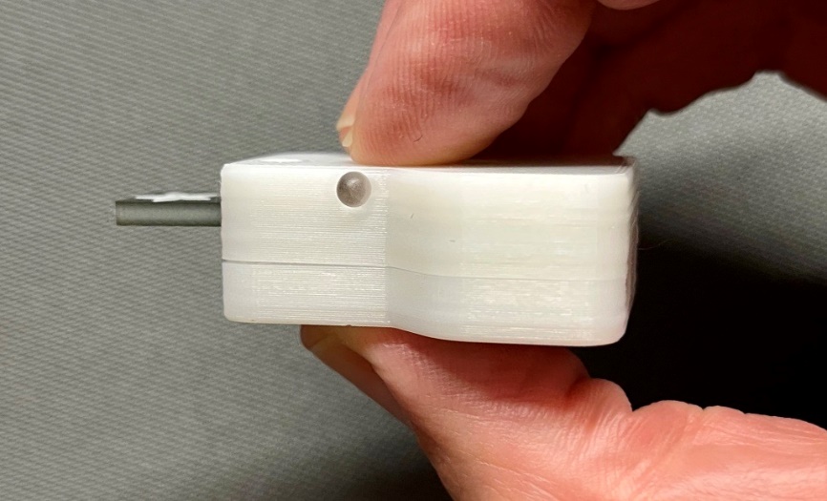
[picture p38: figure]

## Usage

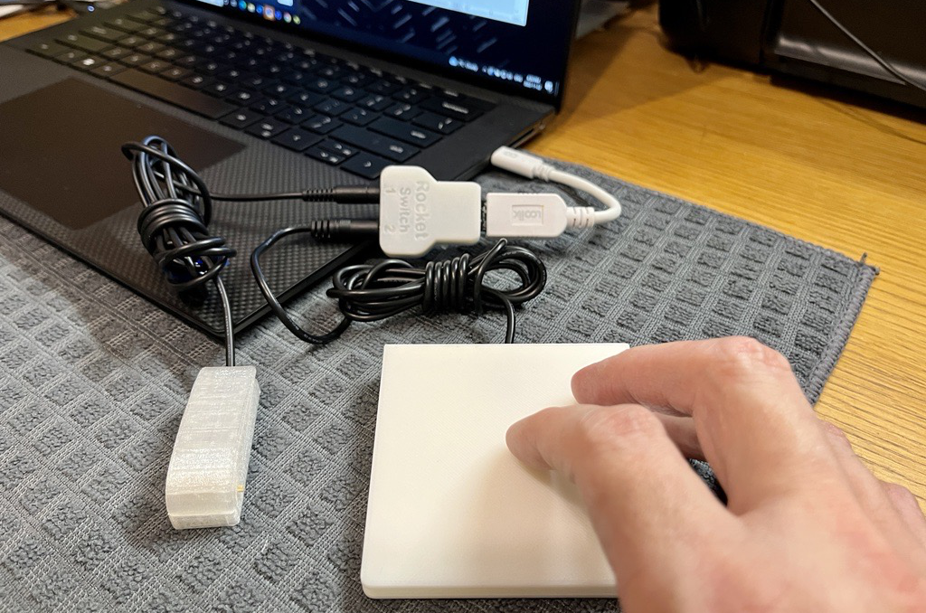
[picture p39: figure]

### Setup

1. Connect an assistive switch to the 3.5 mm audio jack labelled ‘Switch 1’.
2. Connect a second assistive switch to the 3.5 mm audio jack labelled ‘Switch 2’.
3. Locate a USB type A ports on the host device. You may need an adapter cable if your device doesn’t support USB type A.
4. Plug the USB connector of Rocket switch interface to the located USB type A port on your computer or smartphone device.
5. The side mounted LED should turn on, and stay in a teal color, to indicate the device is ready to use.

### Selecting Mode

There are three operating modes and a fourth mode for adjusting the reaction time. The operating mode is indicated by the color of the LED. The operating mode can be changed by cycling through the modes, this is done by pressing and holding Switch 1 for 4 seconds.

Operating Modes
Mode | Mode | Switch 1 Action | Switch 2 Action | LED Color
1 | Switch Mac | Space Key | Enter Key | Teal
2 | Switch | 1 Key | 2 Key | Pink
3 | Mouse | Left Click | Right Click | Purple
4 | Settings | Decrease Reaction Time | Increase Reaction Time | Orange

### Feedback

When a connected assistive switch is pressed, the LED will provide visual feedback.

| | Visual Feedback
| | Input Action
| | Short Press | Long Press (> 4 Seconds)
Input | Switch 1 | Red | Mode Color (Teal, Pink, Purple, Orange)
| Switch 2 | Blue | n/a

### Changing Reaction Time

The Reaction Time can be changed to suit the user’s preferences. The default reaction time is 100 ms. There are 10 different options for Reaction Time.

1. Press and hold Switch 1 for 4 seconds to cycle through the operating modes. Repeat until the LED turns Orange.
2. Short press Switch 1 or Switch 2 to decrease or increase the Reaction Time.

Adjusting Reaction Time
Input | Action | LED
Switch 1 | Decrease Reaction Level | Blinks Red
Switch 2 | Increase Reaction Level | Blinks Blue

3. Press and hold Switch 1 for 4 seconds to return to the desired operating mode.
4. The number of LED blinks indicates the reaction level ( Example: 5 Blinks indicates reaction level 5)

Reaction Time
Reaction Level | Reaction Time
1 | 500 ms
2 | 450 ms
3 | 400 ms
4 | 350 ms
5 | 300 ms
6 | 250 ms
7 | 200 ms
8 | 150 ms
9 (Default) | 100 ms
10 | 50 ms

5. The LED blinks six times in a yellow color when the updated reaction level reaches minimum or maximum reaction level.

## Compatibility

Compatibility
Operating System | Compatible
Windows | Yes
Mac | Yes
Android | Yes
iOS | Yes

## Specifications

Dimensions: 51.1 mm x 33.5 mm x 14.5 mm

## Cleaning

The Rocket-Switch-Interface can be wiped down with a damp cloth Do not submerge the device. Do not expose to high heat.

© 2023 by Neil Squire / Makers Making Change. This work is licensed under the CC BY SA 4.0 License: http://creativecommons.org/licenses/by-sa/4.0 Files available at https://makersmakingchange.com/project/rocket-switch-interface/ Page 2 of 3

V1.2 | February 2024 Rocket-Switch-Interface user Quick Guide

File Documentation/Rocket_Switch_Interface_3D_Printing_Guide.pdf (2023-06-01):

V1.1 | May 2023

## Rocket-Switch-Interface

## 3D PRINTING GUIDE V1.1

© 2023 by Neil Squire / Makers Making Change. This work is licensed under the CC BY SA 4.0 License: http://creativecommons.org/licenses/by-sa/4.0 Files available at https://makersmakingchange.com/project/rocket-switch-interface/

### 3D Printing Summary

Metrics | Configuration #1
Total Print Time (min) | 61
Total Number of Components | 3
Typical Total Mass (g) | 8.65
Typical Number of Print Setups | 1

### 3D Printing Settings

Print File Name | Qty | Total Print Time (hr:min) | Mass (g) | Infill (%) | Support(Y /N) | Layer Height/ Nozzle Diameter(mm) | Notes (orientation, special settings, etc.)
Rocket-Switch-Interface-Bottom-Case.stl | 1 | 0:29 | 4.48 | 15 | N | 0.2/0.4 | -It doesn’t require support - Orient upright so that the screw hole and reset hole are on the print bed.
Rocket-Switch-Interface-Top-Case.stl | 1 | 0:26 | 3.64 | 15 | N | 0.2/0.4 | -It doesn’t require support - Orient upright so that the text is on the print bed.
Rocket-Switch-Interface-Jig.stl | 1 | 0:06 | 0.53 | 15 | N | 0.2/0.4 | -It doesn’t require support - Orient upright so that the rectangular cut is on the print bed.

## 3D PRINTING GUIDE V1.1

### Post-Processing

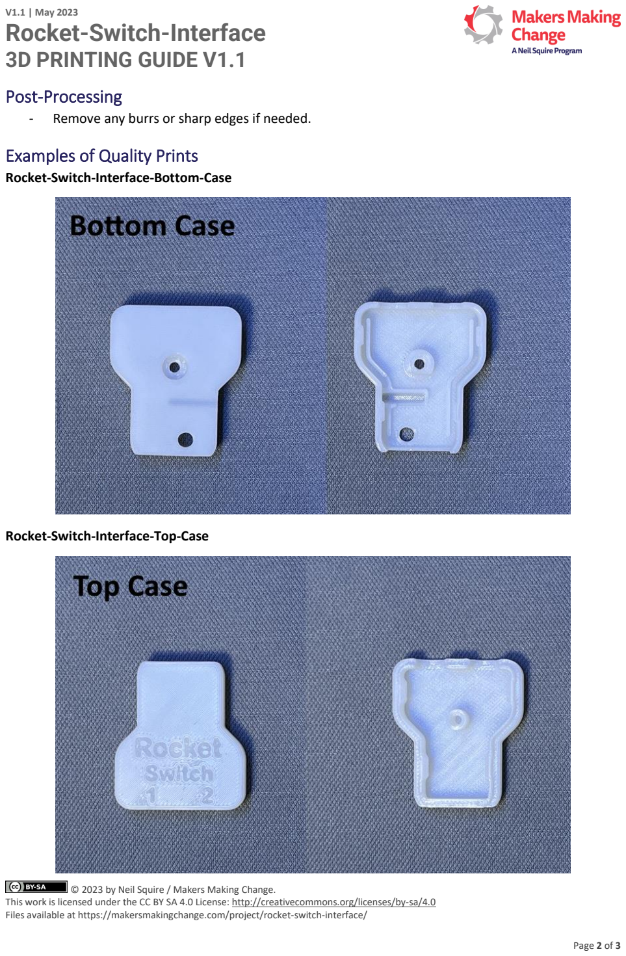
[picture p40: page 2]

© 2023 by Neil Squire / Makers Making Change. This work is licensed under the CC BY SA 4.0 License: http://creativecommons.org/licenses/by-sa/4.0

- Remove any burrs or sharp edges if needed.

### Examples of Quality Prints

Rocket-Switch-Interface-Bottom-Case

Rocket-Switch-Interface-Top-Case

## 3D PRINTING GUIDE V1.1

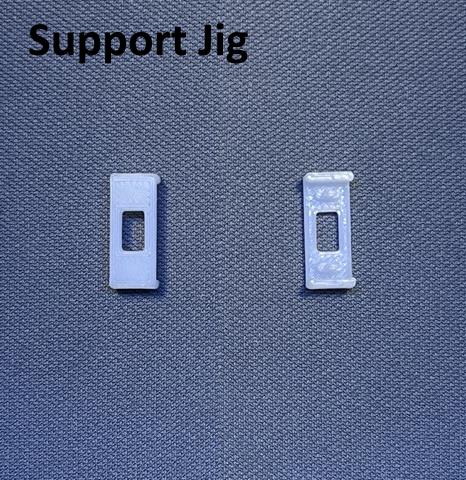
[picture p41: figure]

© 2023 by Neil Squire / Makers Making Change. This work is licensed under the CC BY SA 4.0 License: http://creativecommons.org/licenses/by-sa/4.0

Rocket-Switch-Interface-Jig

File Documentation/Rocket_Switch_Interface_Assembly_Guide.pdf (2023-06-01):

V1.1 | May 2023

## Rocket-Switch-Interface

## ASSEMBLY GUIDE V1.1

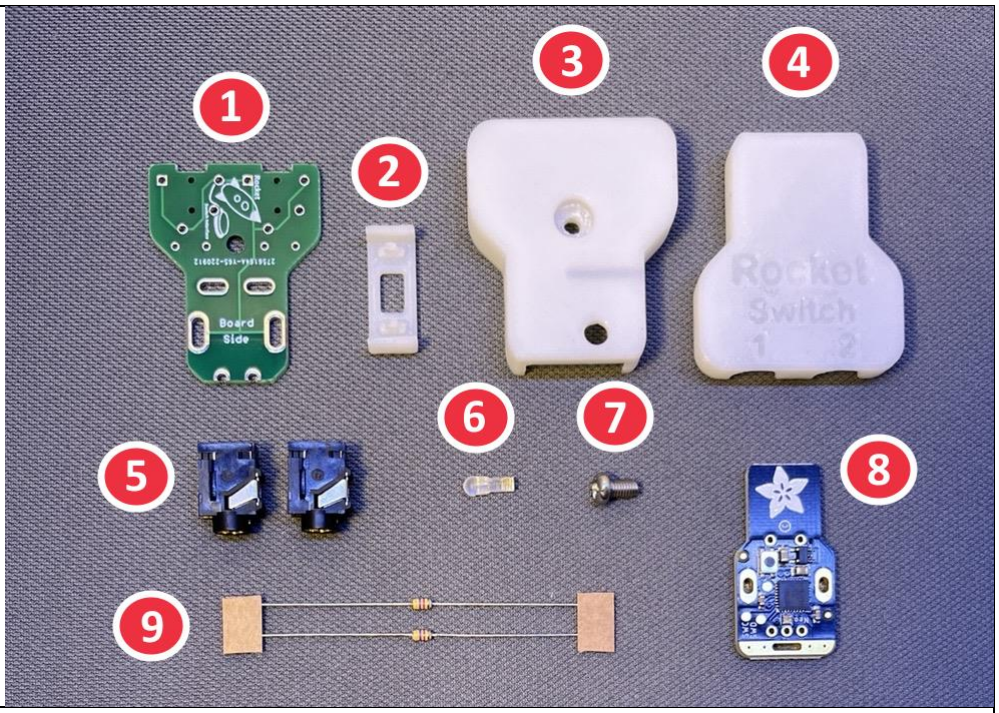
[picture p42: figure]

© 2023 by Neil Squire / Makers Making Change. This work is licensed under the CC BY SA 4.0 License: http://creativecommons.org/licenses/by-sa/4.0 Files available at https://makersmakingchange.com/project/rocket-switch-interface/

### Required Components

BOM
1. Rocket-Switch-Interface PCB (Printed Circuit Board)
2. 3D Printed Assembly Jig
3. Rocket-Switch-Interface Bottom Case
4. Rocket-Switch-Interface Top Case
5. SJ-43514 3.5mm Jack Stereo x 2
6. Light Pipe
7. M3 8MM Phillip Machine Screw
8. Adafruit Rotary Trinkey
9. 4.7K Through-Hole Resistor x 2

## ASSEMBLY GUIDE V1.1

© 2023 by Neil Squire / Makers Making Change. This work is licensed under the CC BY SA 4.0 License: http://creativecommons.org/licenses/by-sa/4.0

### Required Tools

- Temperature regulated soldering Iron.

### Required Personal Protective Equipment (PPE)

- Lexan (polycarbonate) safety glasses
- Disposable examination gloves (Optional- rosin residue may irritate sensitive skin)

## ASSEMBLY GUIDE V1.1

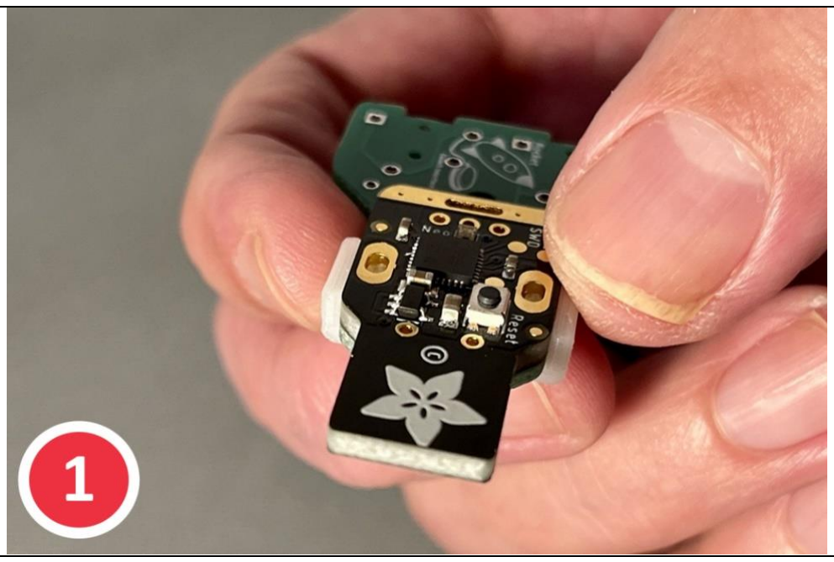
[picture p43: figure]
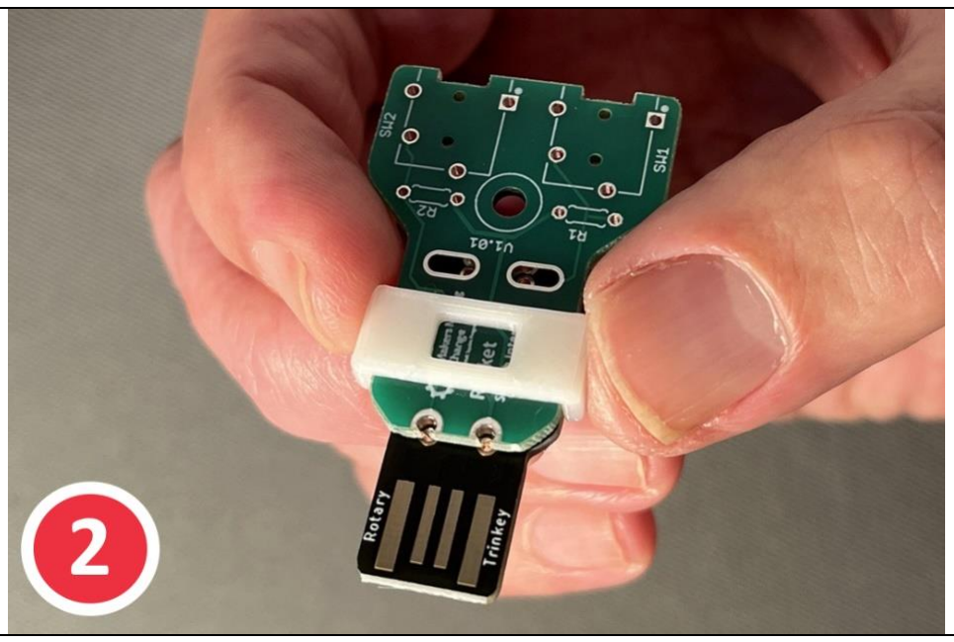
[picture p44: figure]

© 2023 by Neil Squire / Makers Making Change. This work is licensed under the CC BY SA 4.0 License: http://creativecommons.org/licenses/by-sa/4.0

### Assembly Instructions

### Step 1

Clip the Assembly Jig firmly onto the component side of the Rocket Switch PCB. Ensure the posts of the Jig go through the two oval holes.

### Step 2

While keeping the jig securely clipped in place, flip The PCB over to the solder side of the PCB. This is the side that has a small rocket ship logo, and text that says “Board side” to mark space reserved for the Rotary Trinkey board.

## ASSEMBLY GUIDE V1.1

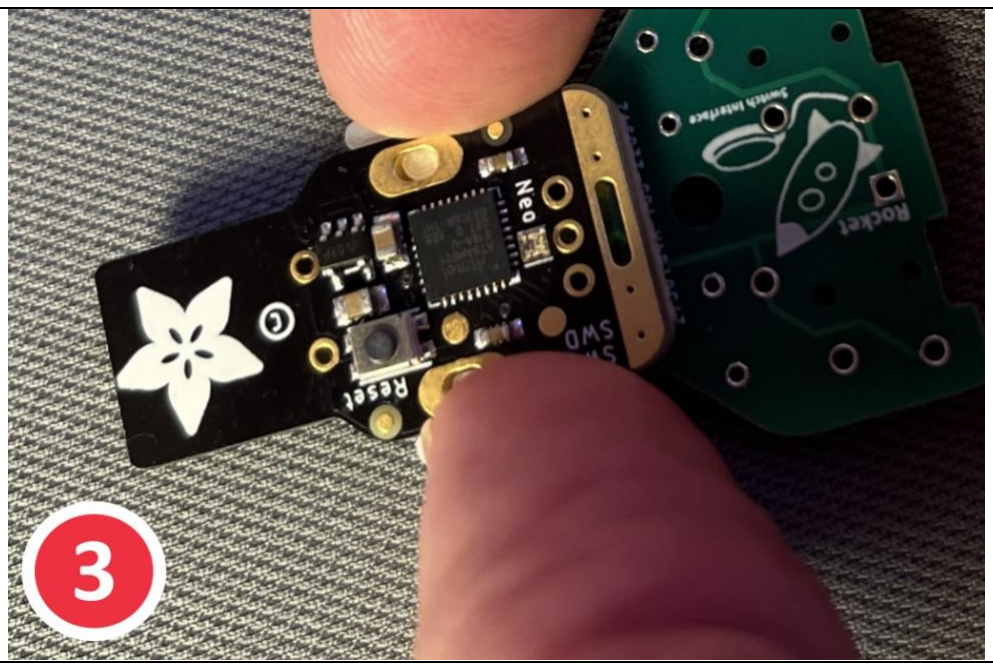
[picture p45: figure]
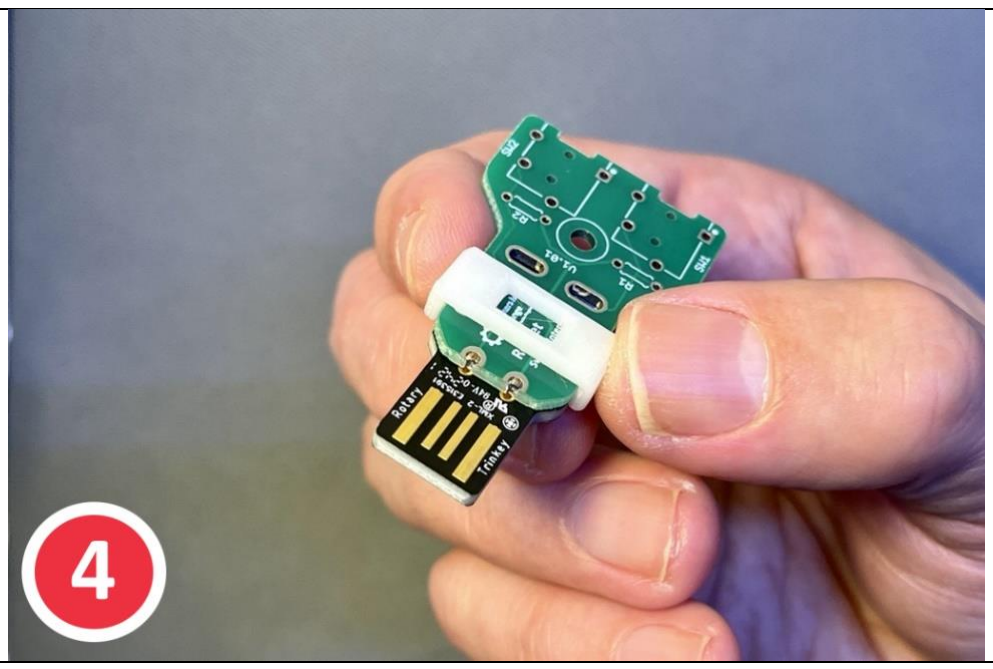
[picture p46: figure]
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

### Step 3

Place the flat side of the Trinkey board onto the protruding clip posts, as shown in the image below. The Trinkey board should kept flat against the Rocket switch board.

### Step 4

Flip the board back to the component side, while again keeping the boards clipped flat together.

## ASSEMBLY GUIDE V1.1

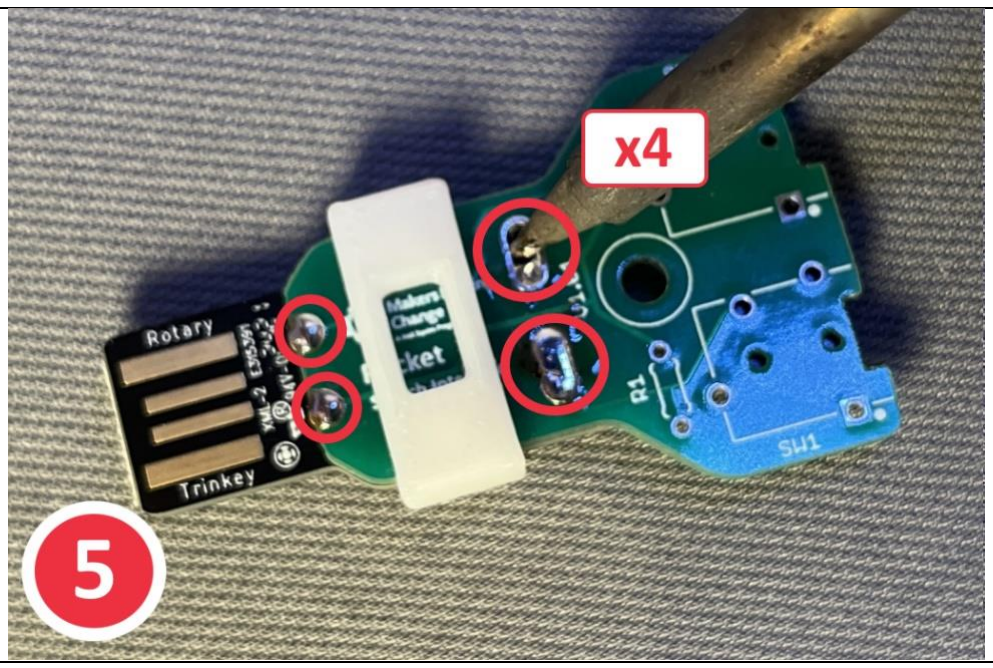
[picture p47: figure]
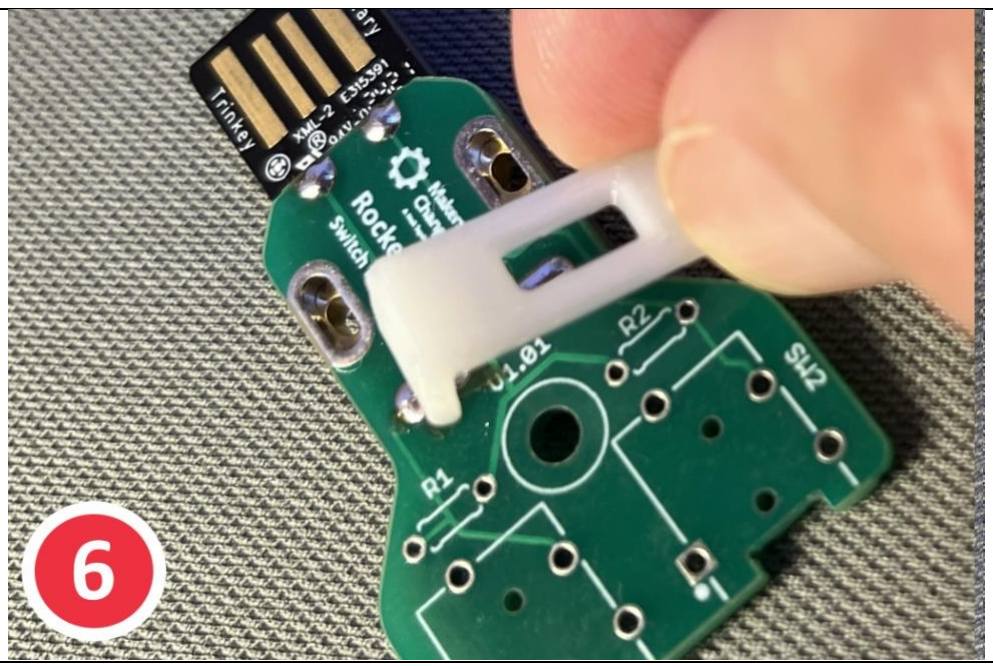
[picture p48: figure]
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

### Step 5

Using a soldering iron and rosin core solder, fill one of the large oval holes with solder while maintaining the boards positioned together flat (no gap). Inspect the boards to confirm the boards are flush and straight. If so, solder fill the two round holes adjacent to the USB connector, and the remaining large oval hole.

### Step 6

Remove the jig clip from the two joined PCBs, as its task is complete. If you have access to a PLA plastic recycling bin, please place it there.

## ASSEMBLY GUIDE V1.1

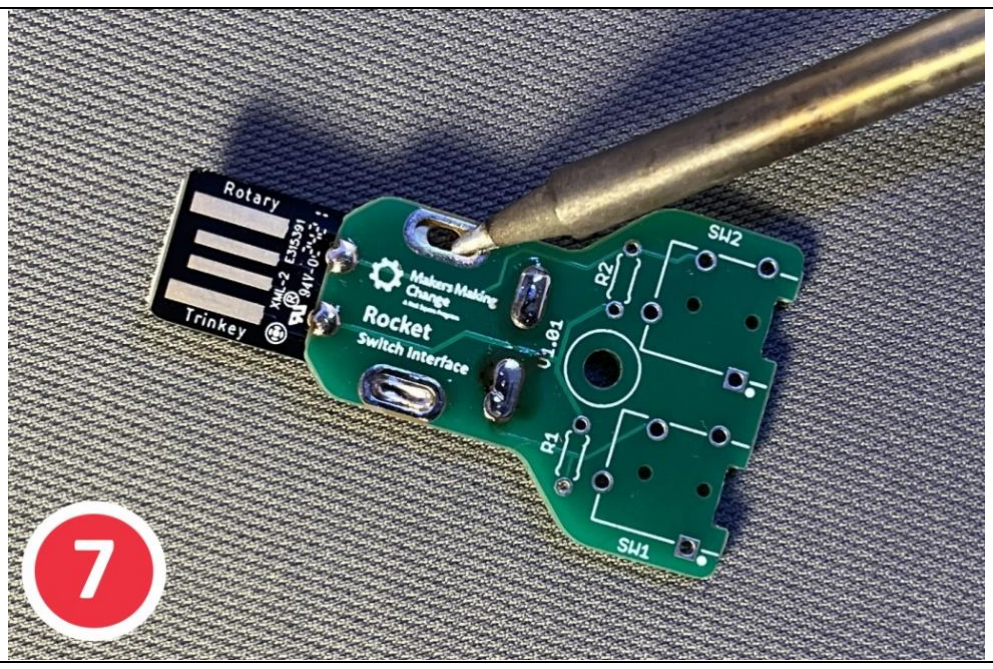
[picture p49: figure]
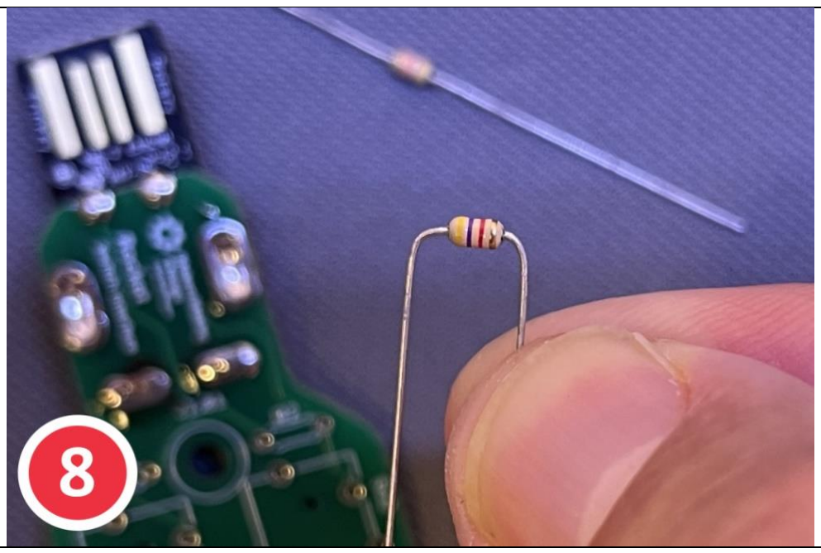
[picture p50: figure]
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

### Step 7

Solder fill the two oval holes that were occupied by the posts on the jig.

### Step 8

Bend the leads of both 4.7K resistors (90 degrees), so that they appear as shown in the image below.

## ASSEMBLY GUIDE V1.1

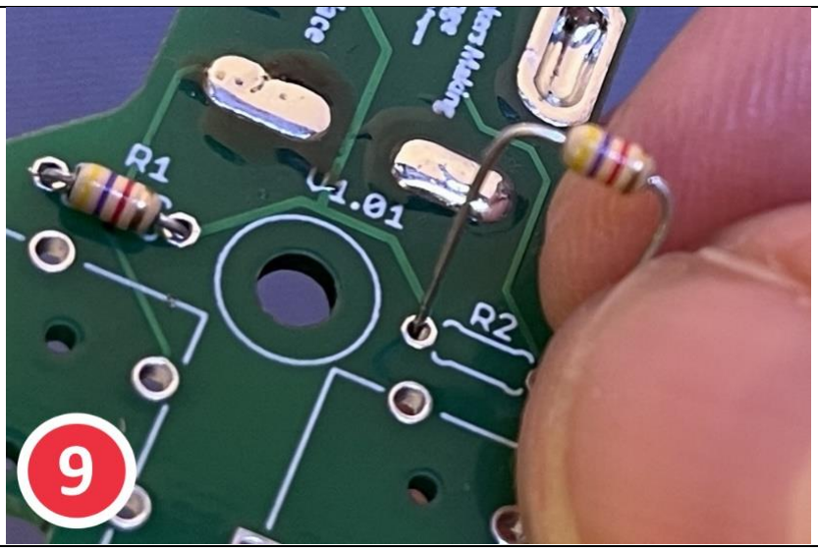
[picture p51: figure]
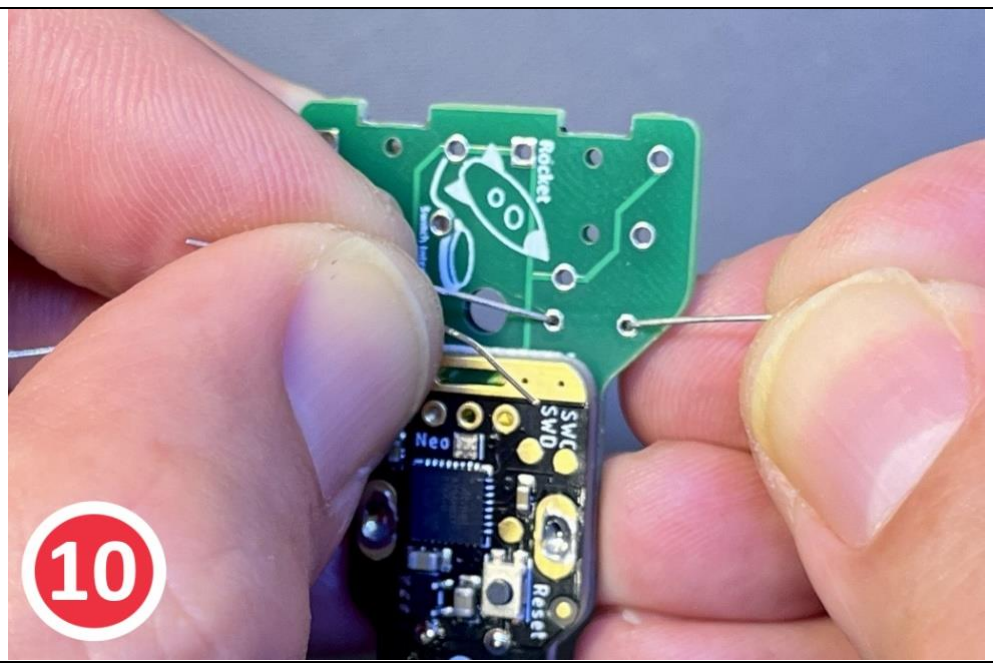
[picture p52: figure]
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

### Step 9

Install both resistors into their respective locations marked “R1” and “R2” on the component side of the PCB (shown below), keeping each resistor against the PCB.

### Step 10

Bend the inserted wires apart (45 degrees) on the solder side of the PCB. This will help keep the resistors in place for soldering (next step).

## ASSEMBLY GUIDE V1.1

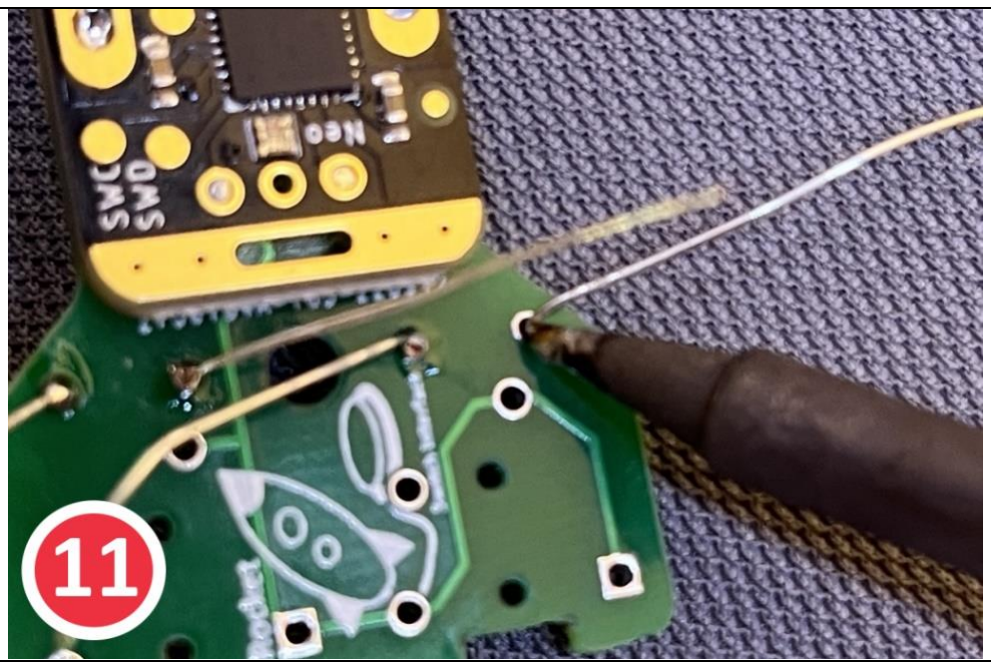
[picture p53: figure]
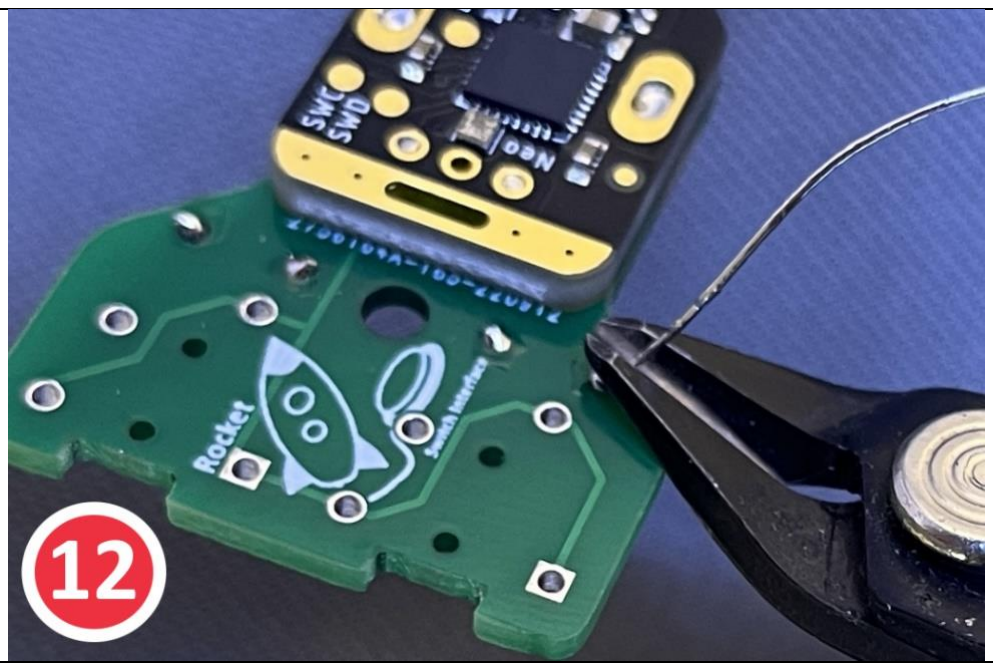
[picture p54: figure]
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

### Step 11

Using the soldering iron, apply solder to all resistor wire holes.

### Step 12

Using side cutters, trim all the resistor wire leads flush with the top of each solder joint.

## ASSEMBLY GUIDE V1.1

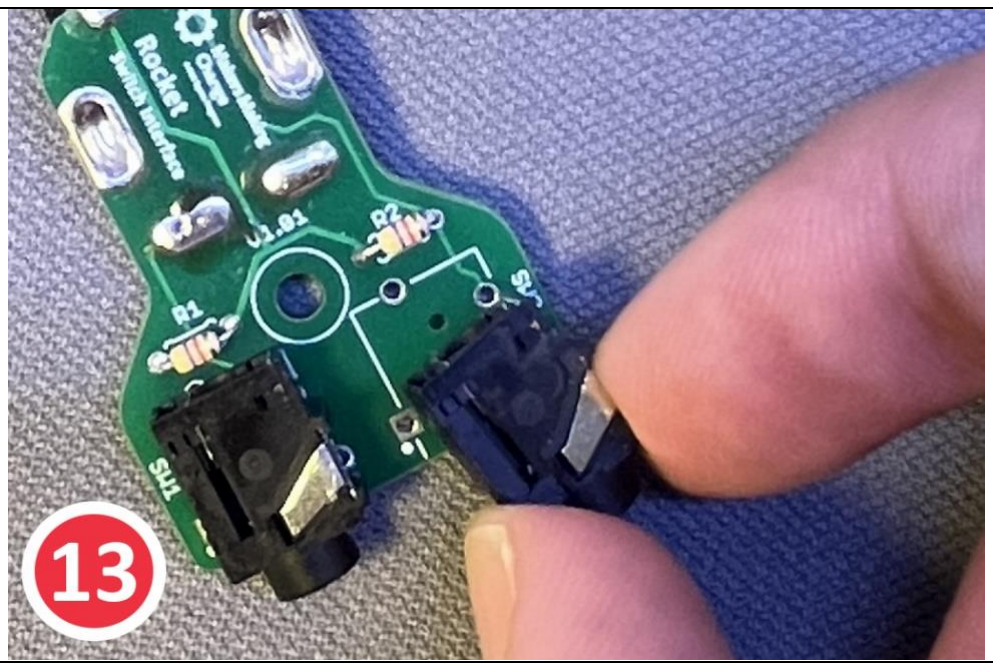
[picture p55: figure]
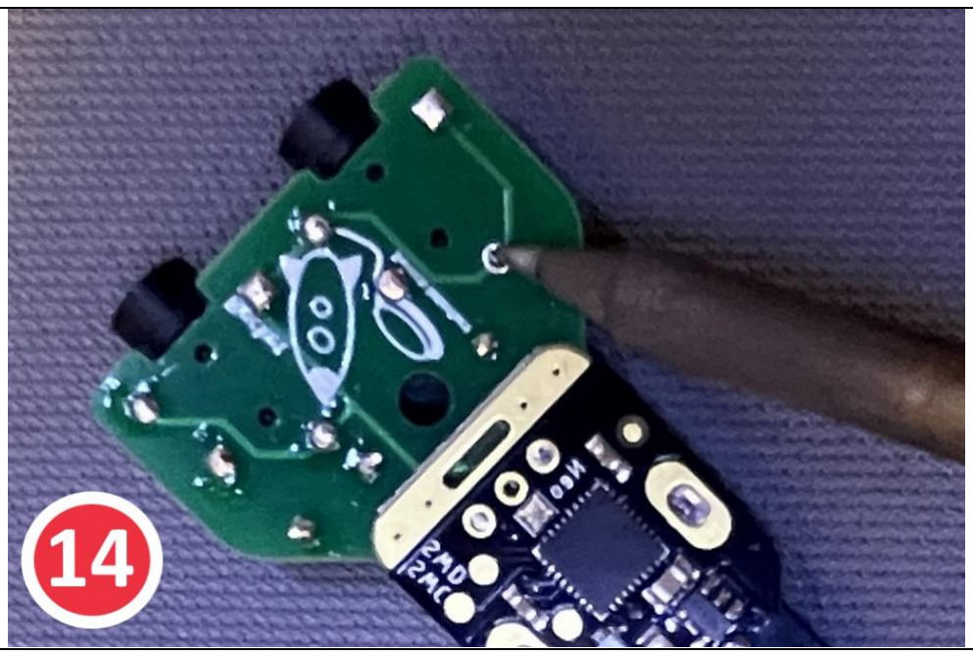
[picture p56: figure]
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

### Step 13

Insert the two jacks into locations SW1 and SW2 on the component side of the PCB. Keep the jacks held in place with your fingers and flip the PCB in preparation for soldering.

### Step 14

Confirm the jacks remain firmly against the Rocket Switch PCB, as you solder the four jack pins on each jack to the PCB. This completes all the soldering steps for this project.

## ASSEMBLY GUIDE V1.1

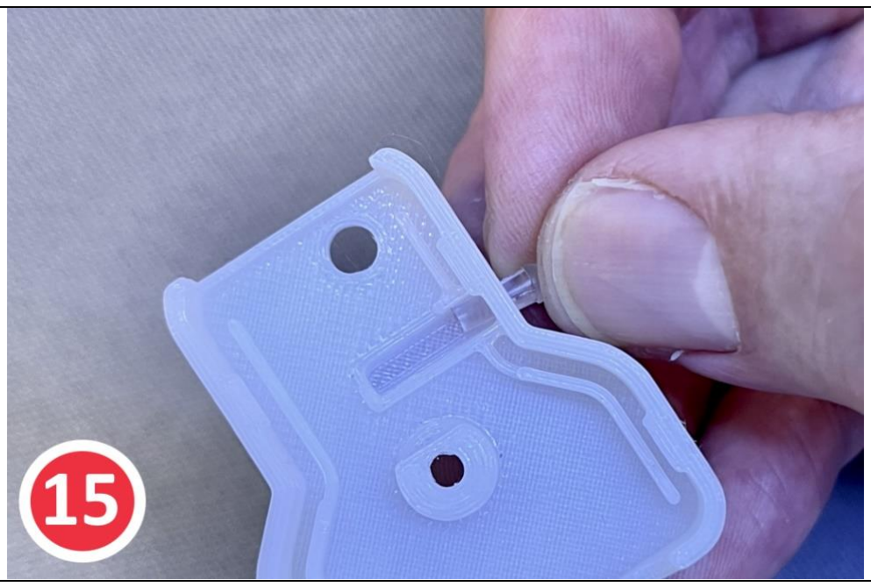
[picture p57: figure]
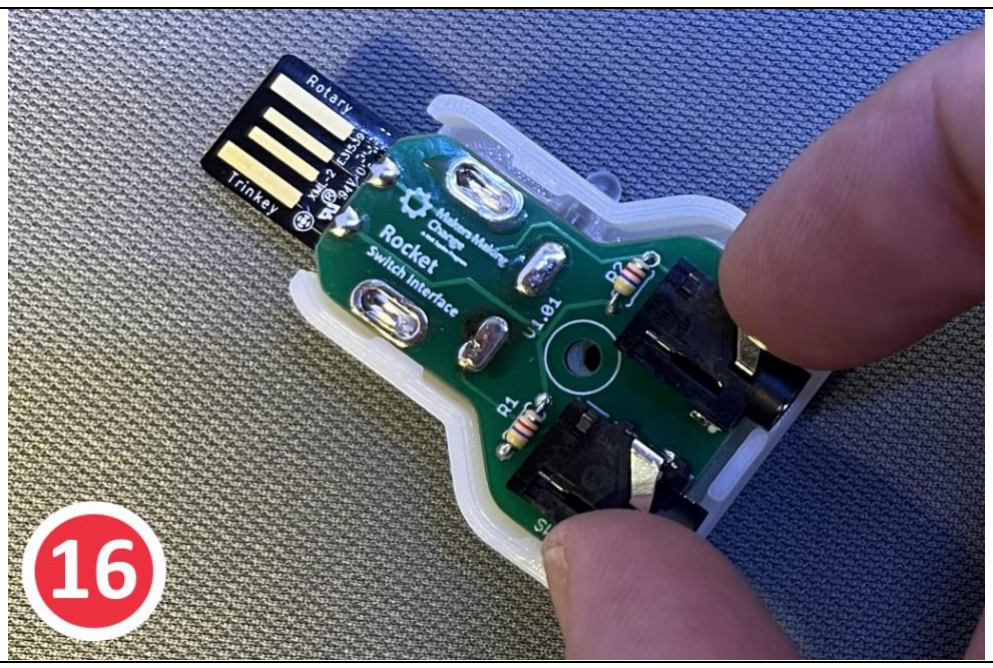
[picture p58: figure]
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

### Step 15

Prepare the lower shell of the Rocket Switch case by inserting the light pipe into the side hole. The light pipe should be inserted until only the half sphere tip protrudes from the case.

### Step 16

Insert the Rocket Switch assembly into the bottom case. Ensure the jack ends are resting in the U-shaped half holes of the case, as shown.

## ASSEMBLY GUIDE V1.1

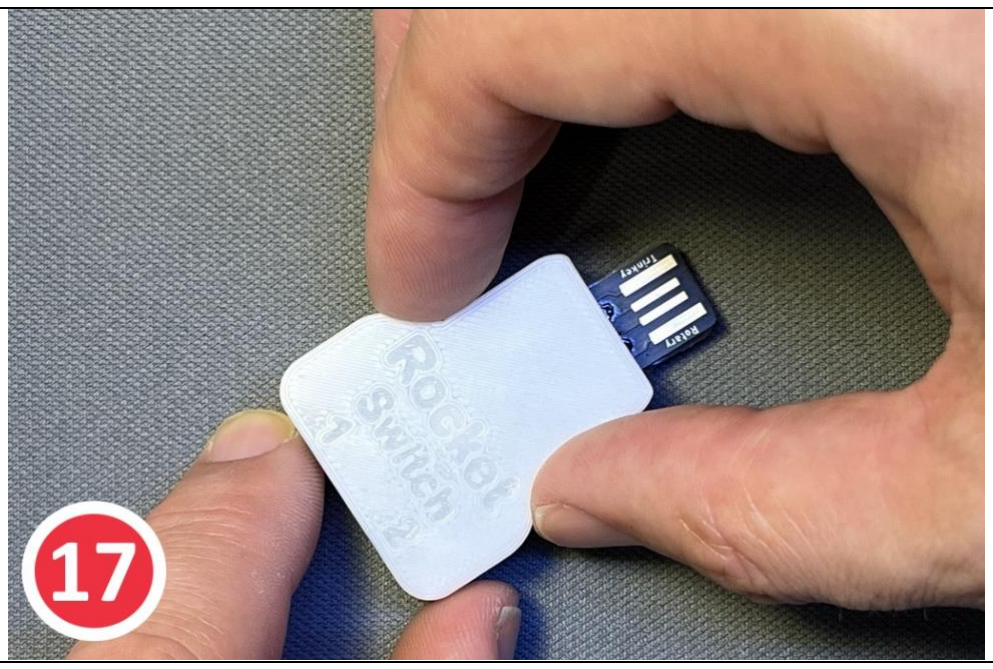
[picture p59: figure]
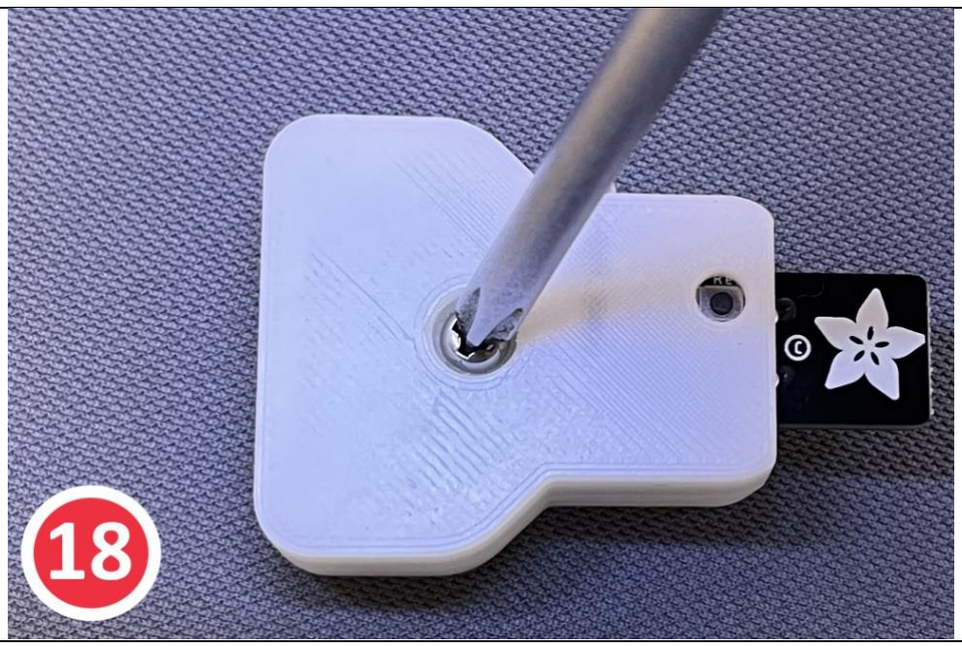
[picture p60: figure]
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

### Step 17

Align the top case with the lower case edge, then push down until it snaps together with the lower one.

### Step 18

Flip the encased Rocket Switch unit to gain access to the screw hole. Install the M3 X 8 mm screw into the hole with a Phillips screwdriver until it is snug. Do not overtighten.

## ASSEMBLY GUIDE V1.1

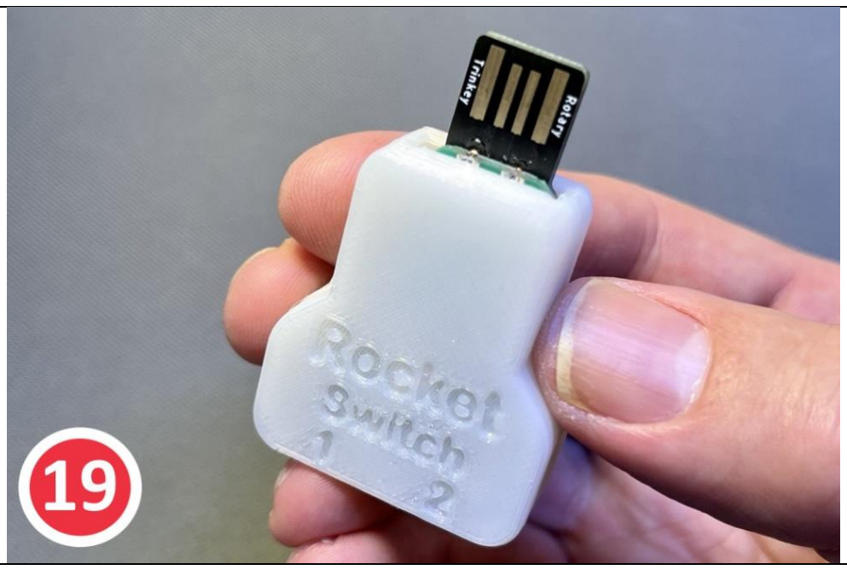
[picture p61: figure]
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

### Step 19

The physical construction of the Rocket switch is now complete. If the firmware's been pre-installed, then there’s nothing more to do. Otherwise, flash the current firmware onto the Rocket switch prior to being used. See the Software Setup section (below) for instruction on this.

## ASSEMBLY GUIDE V1.1

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

### Software Setup

The Rocket-Switch-Interface software can be downloaded from the Rocket-Switch-Interface GitHub repository under Build_Files > Software_Files directory.

### Installing Arduino IDE

The Arduino IDE is required to compile and upload the source code to the Adafruit Rotary Trinkey board. You can download and install the Arduino from official Arduino website that you can find using following link:

https://www.arduino.cc/en/software

### Installing Arduino Libraries

The following instructions on how to install additional Arduino libraries helps you to get started with setting up Arduino IDE with required libraries and dependencies.

https://www.arduino.cc/en/guide/libraries

Board Support Packages
You can find the official instructions to install Board Support Packages on Adafruit website using following link:

https://learn.adafruit.com/adafruit-qt-py/arduino-ide-setup

Alternatively, you can perform following instructions to install Board Support Packages:

1. Open and start the Arduino IDE.
2. Go to File > Preferences.
3. Add following link as a new line under Additional Board Manager URLs
- https://adafruit.github.io/arduino-board-index/package_adafruit_index.json
4. Restart the Arduino IDE
5. Open the Boards Manager option from the Tools > Board menu and install Adafruit SAMD Boards by Adafruit
6. Wait until the IDE finishes installing the cross-compiling toolchain and tools associated with Board Support Package. This may take few minutes.
7. That’s it! The installation of Board Support Packages is finished.

## ASSEMBLY GUIDE V1.1

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

Required Software and libraries
- StopWatch library (https://github.com/RobTillaart/Stopwatch_RT)
- Adafruit_NeoPixel library (https://github.com/adafruit/Adafruit_NeoPixel)
- FlashStorage library (https://github.com/cmaglie/FlashStorage)
- Rocket_Switch_Interface.ino (https://github.com/makersmakingchange/Rocket-Switch-Interface/blob/main/Build_Files/Software_Files/Rocket_Switch_Interface/Rocket_Switch_Interface.ino)

You can use the following instructions to download and install the required libraries:

1) Visit the StopWatch library (https://github.com/RobTillaart/Stopwatch_RT) github repository page.
2) Click on Code > Download Zip to download StopWatch library.
3) Extract Stopwatch_RT-master.zip file
4) Rename Stopwatch_RT-master folder to Stopwatch folder under Stopwatch_RT-master subdirectory.
5) Copy or move Stopwatch folder to Arduino installation library subdirectory. As an example: This is found under C:\Program Files (x86)\Arduino\libraries in windows 10.
6) Visit the FlashStorage library (https://github.com/cmaglie/FlashStorage) github repository page.
7) Click on Code > Download Zip to download FlashStorage library.
8) Extract FlashStorage-master.zip file
9) Rename FlashStorage-master folder to FlashStorage folder under FlashStorage-master subdirectory.
10) Copy or move FlashStorage folder to Arduino installation library subdirectory. As an example: This is found under C:\Program Files (x86)\Arduino\libraries in windows 10.
11) Visit the Rocket_Switch_Interface.ino (https://neilsquiresoc.sharepoint.com/sites/MMC-RD/Shared%20Documents/RD%2022-08%20Rocket%20Switch%20Interface/Rocket-Switch-Interface/Documentation/Working_Do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) raw source code file under Rocket-Switch-Interface github repository page.
12) Right click on the source code or any place on this page and select Save Page As…
13) Select the directory you would like to save the software in your computer.
14) Change File name from Rocket_Switch_Interface to Rocket_Switch_Interface.ino
15) Change Save as type to All Files.
16) Click on Save button.
17) Open the directory you selected in step 13.
18) Double left click or open Rocket_Switch_Interface file
19) Arduino IDE will ask your permission to create a new sketch folder named Rocket_Switch_Interface and move Rocket_Switch_Interface.ino under this folder.
20) Click on the Ok button.
21) Arduino IDE should now open the Rocket_Switch_Interface.ino file automatically.

## ASSEMBLY GUIDE V1.1

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

Uploading Software
Note: Make sure all files are included in your local copy of Software directory before uploading it to the Adafruit Rotary Trinkey board. The libraries can be installed in Arduino libraries..
1. Start the Arduino IDE
2. Open Rocket_Switch_Interface.ino
3. Select the Board under Tools > Board > Adafruit SAMD Boards as Adafruit Rotary Trinkey (SAMD21)
4. Select Arduino as USB Stack under Tools > USB Stack
5. Select the correct port number under Tools > Port which should show COM XX (Adafruit Rotary Trinkey)

Note: It’s very important to make sure the correct Board and port number are selected as selecting the wrong board may result problems with bootloader of Adafruit Rotary Trinkey board.

6. Press the Verify button to make sure there is no problem with the software and libraries.
7. Press Upload button

You can now upload the software, Arduino IDE will show you a Done Uploading message indicating the software is uploaded to your Rocket-Switch-Interface.

The LED on the Adafruit Rotary Trinkey board blinks two times in teal to indicate the start of initialization process has been started and it will blink again two times in green to indicate end of the initialization process.

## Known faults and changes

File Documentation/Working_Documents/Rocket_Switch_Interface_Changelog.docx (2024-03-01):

# Version 1.0 | 2022-Oct-28

- Initial release
  - Software includes HID keyboard (Switch Access) , HID Mac keyboard (Mac Switch Access) and HID mouse operation mode
  - Software includes a settings mode which allows the user to adjust reaction time
  - 3D printed enclosure
    - The bottom case was updated to include a light pipe
  - Software includes a method to change the operation mode

© 2022 by Neil Squire / Makers Making Change. This work is licensed under the CC BY SA 4.0 License: http://creativecommons.org/licenses/by-sa/4.0 Files available at https://makersmakingchange.com/project/rocket-switch-interface/ Page 1 of 1

V1.0 | October 2022 Rocket-Switch-Interface changelog V1.0

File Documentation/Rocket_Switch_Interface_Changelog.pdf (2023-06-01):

V1.1 | May 2023

## Rocket-Switch-Interface

## CHANGELOG V1.1

© 2023 by Neil Squire / Makers Making Change. This work is licensed under the CC BY SA 4.0 License: http://creativecommons.org/licenses/by-sa/4.0 Files available at https://makersmakingchange.com/project/rocket-switch-interface/

## Version 1.0 | Date 28/10/2022

- Software includes HID keyboard ( Switch Access ) , HID Mac keyboard ( Mac Switch Access ) and HID mouse operation mode
- Software includes a settings mode which allows the user to adjust reaction time.
- The bottom case was updated to include a light pipe.
- Software includes a method to change the operation mode.

## Version 1.1 | Date 30/05/2023

- Updated the 3D Printed top case and bottom case to increase tolerance for variety of 3D Printer.
- Included maker feedback in the updated assembly guide.
- Changed screw length from M3 6MM to M3 8MM.

V1.1 | May 2023

## Rocket-Switch-Interface

## CHANGELOG V1.1

© 2023 by Neil Squire / Makers Making Change. This work is licensed under the CC BY SA 4.0 License: http://creativecommons.org/licenses/by-sa/4.0 Files available at https://makersmakingchange.com/project/rocket-switch-interface/

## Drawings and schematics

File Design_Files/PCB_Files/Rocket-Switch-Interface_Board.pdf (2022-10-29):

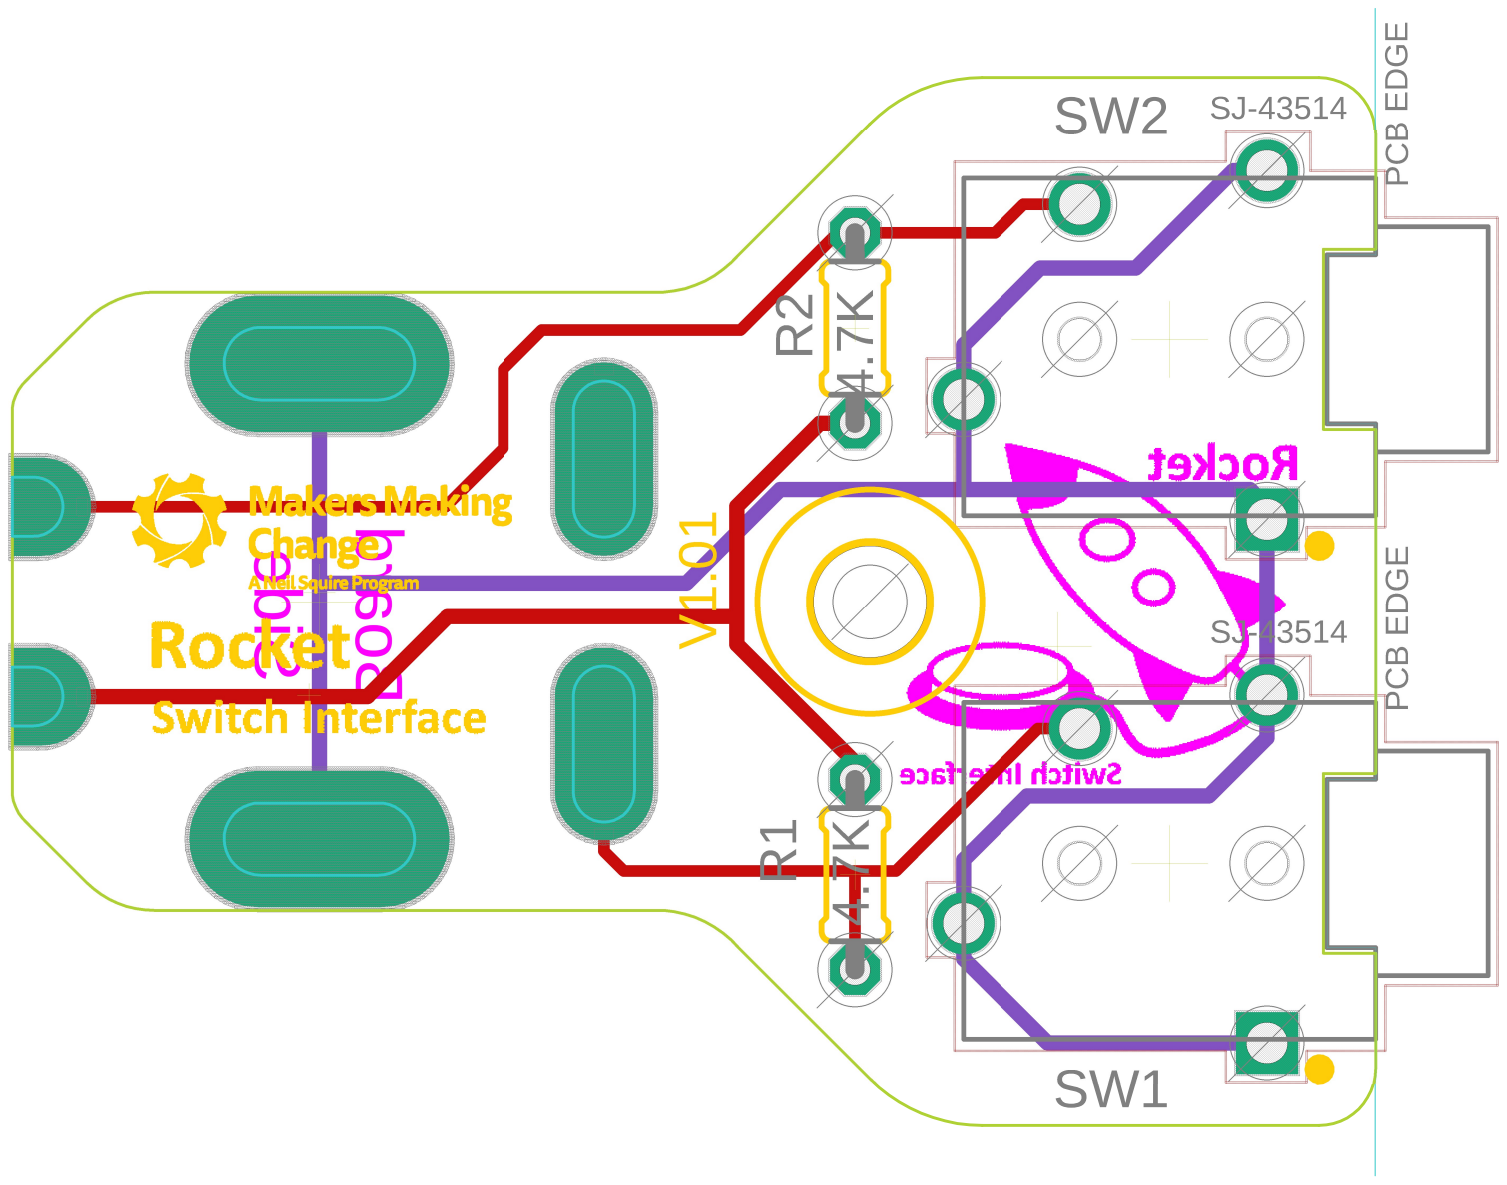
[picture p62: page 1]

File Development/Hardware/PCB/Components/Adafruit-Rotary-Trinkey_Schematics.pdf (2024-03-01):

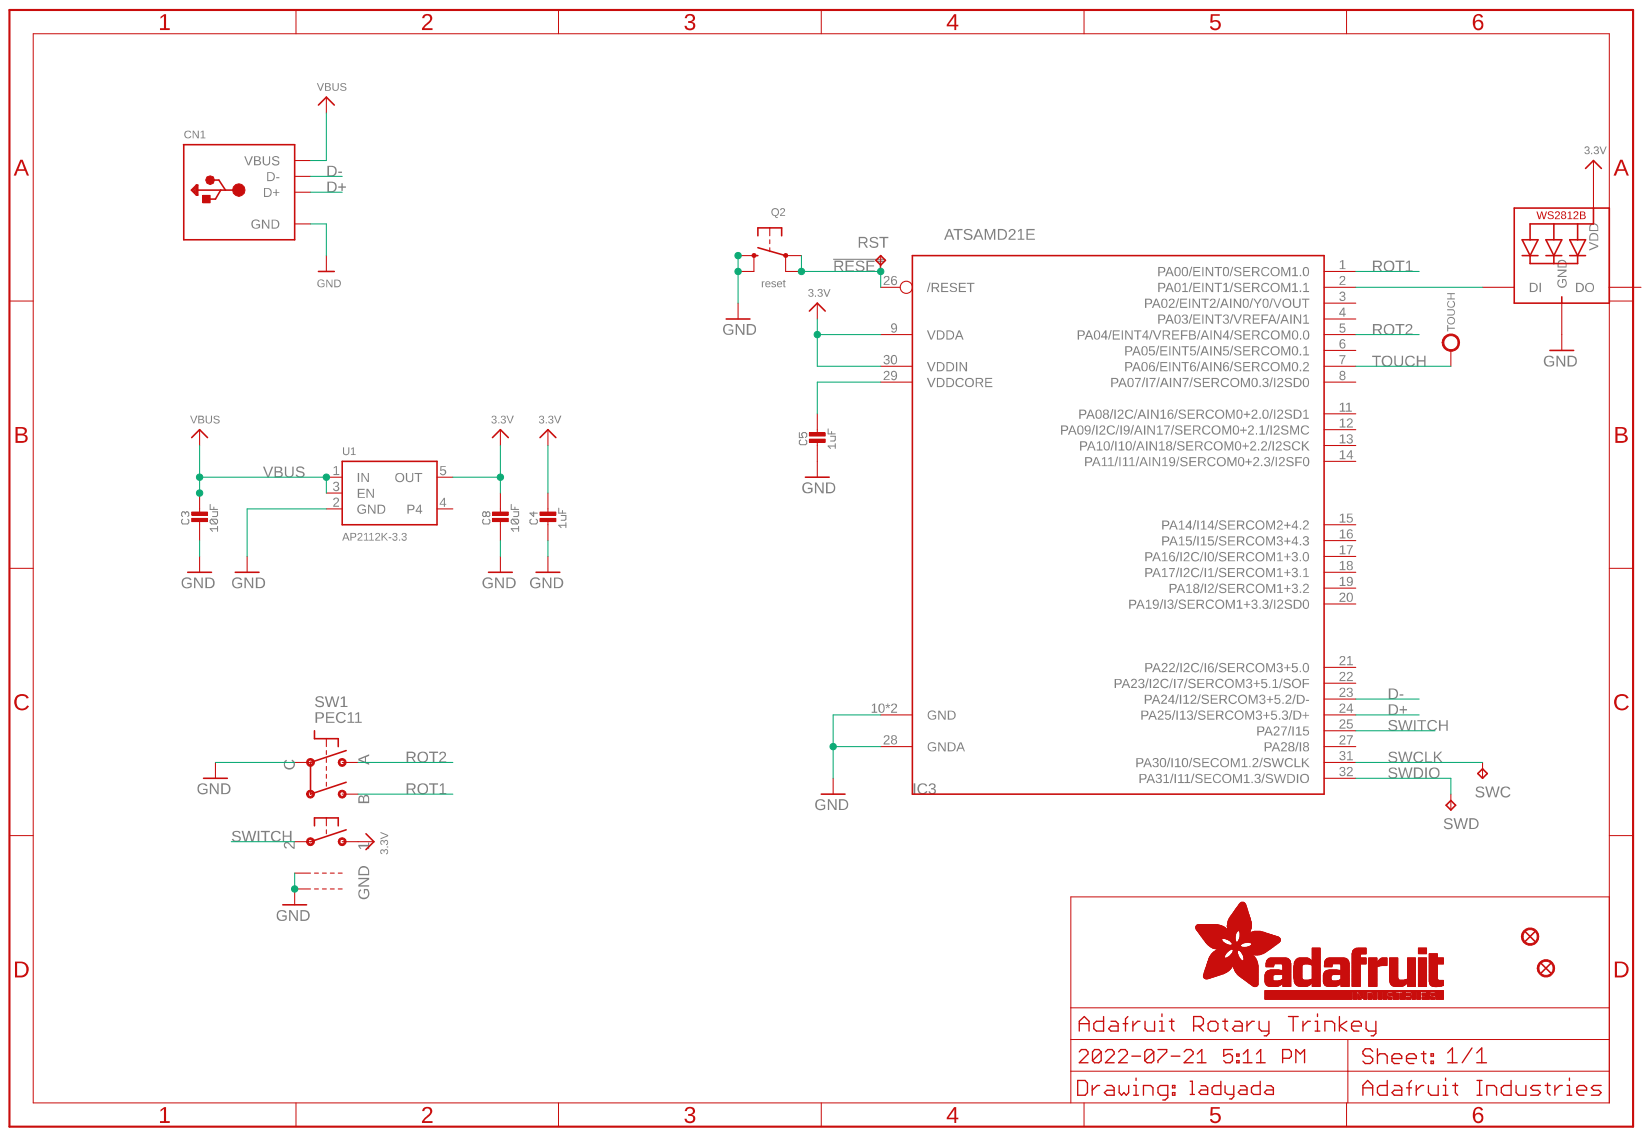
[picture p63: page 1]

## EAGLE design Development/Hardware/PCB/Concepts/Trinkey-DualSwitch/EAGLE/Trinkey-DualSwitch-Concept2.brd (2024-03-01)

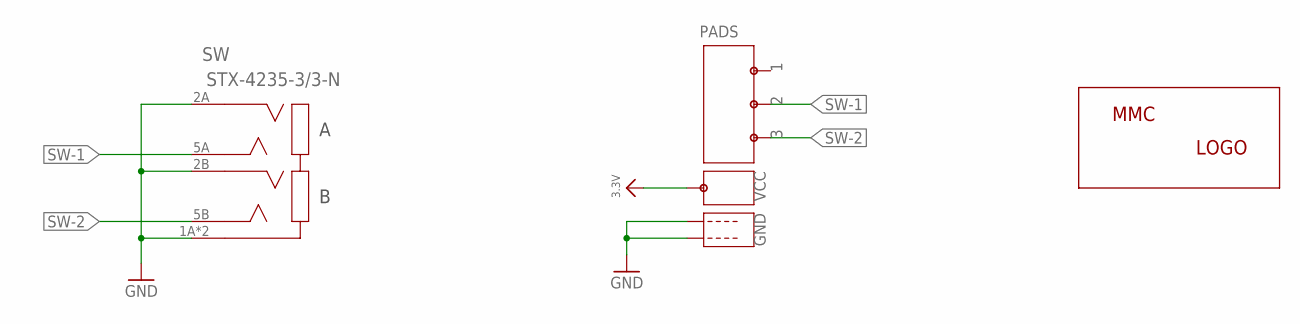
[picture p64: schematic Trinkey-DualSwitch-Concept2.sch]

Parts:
LABEL_LOGO: MMC_LOGO-XSM; MMC_X-SMALL_LOGO
PADS: CASTELLATED-ROTARY-TRINKEY
SW: STX-4235-3/3-N; STX-4235-3/3

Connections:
3.3V: PADS.P$VCC
GND: PADS.P$GND1, PADS.P$GND2, SW.1A (1AB), SW.1B (1AB), SW.2A, SW.2B
SW-1: PADS.P$S2, SW.5A
SW-2: PADS.P$S3, SW.5B

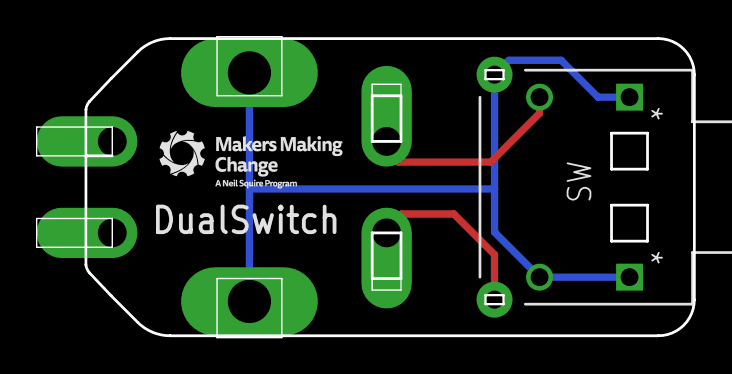
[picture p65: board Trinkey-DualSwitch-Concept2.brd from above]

Board: 2 copper layers, 36.5 x 16.7 mm, 3 parts (1 on the bottom side), 3 nets.

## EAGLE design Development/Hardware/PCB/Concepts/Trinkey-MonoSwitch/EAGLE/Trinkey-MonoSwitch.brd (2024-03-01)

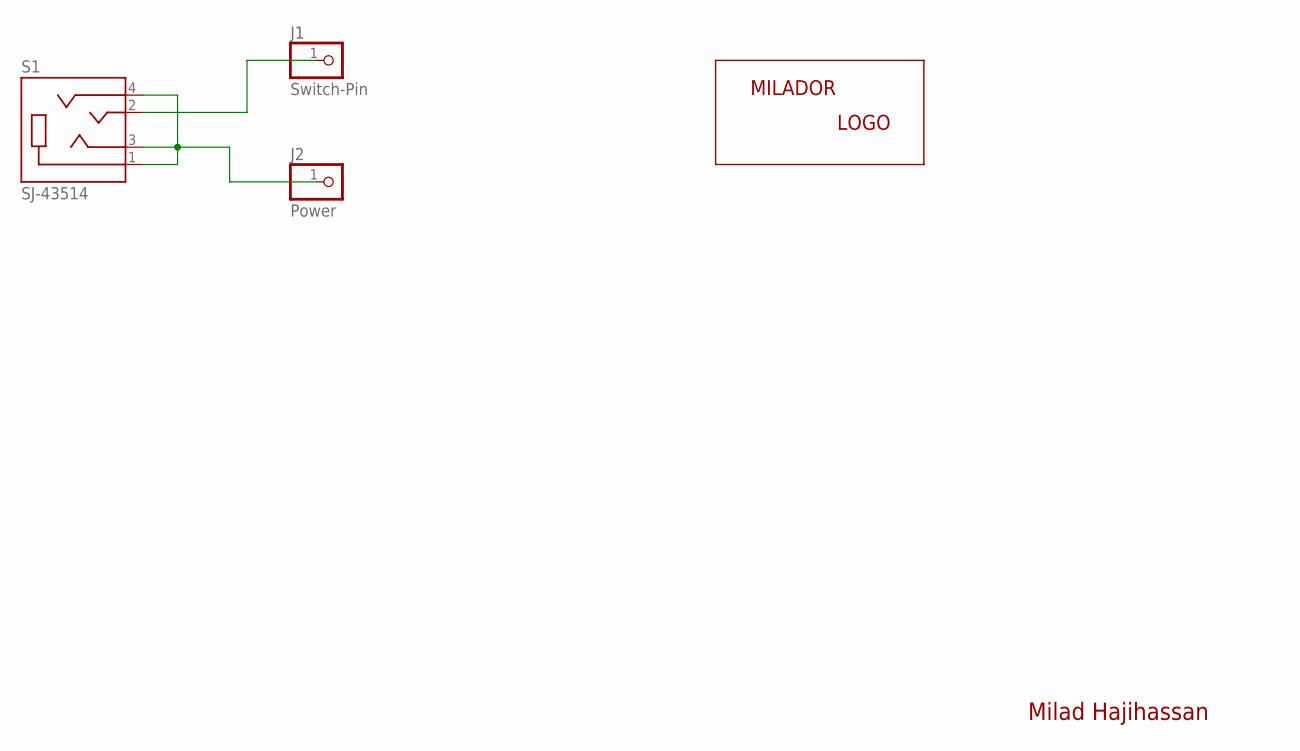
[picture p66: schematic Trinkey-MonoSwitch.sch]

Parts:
J1: Switch-Pin; CASTELLATED_PIN-1X01
J2: Power; CASTELLATED_PIN-1X01
LABEL-LOGO: MILADOR-LOGO-SM; MILADOR_LOGO2
S1: SJ-43514; CUI_SJ-43514

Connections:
unnamed: J1.1, S1.2 (TIP)
unnamed: J2.1, S1.1 (SLEEVE), S1.3 (RING1), S1.4 (RING2)

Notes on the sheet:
Milad Hajihassan

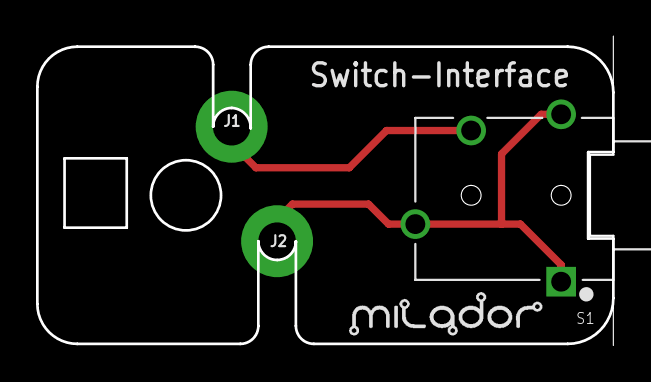
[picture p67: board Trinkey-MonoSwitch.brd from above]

Board: 2 copper layers, 32.0 x 17.2 mm, 4 parts (0 on the bottom side), 2 nets.

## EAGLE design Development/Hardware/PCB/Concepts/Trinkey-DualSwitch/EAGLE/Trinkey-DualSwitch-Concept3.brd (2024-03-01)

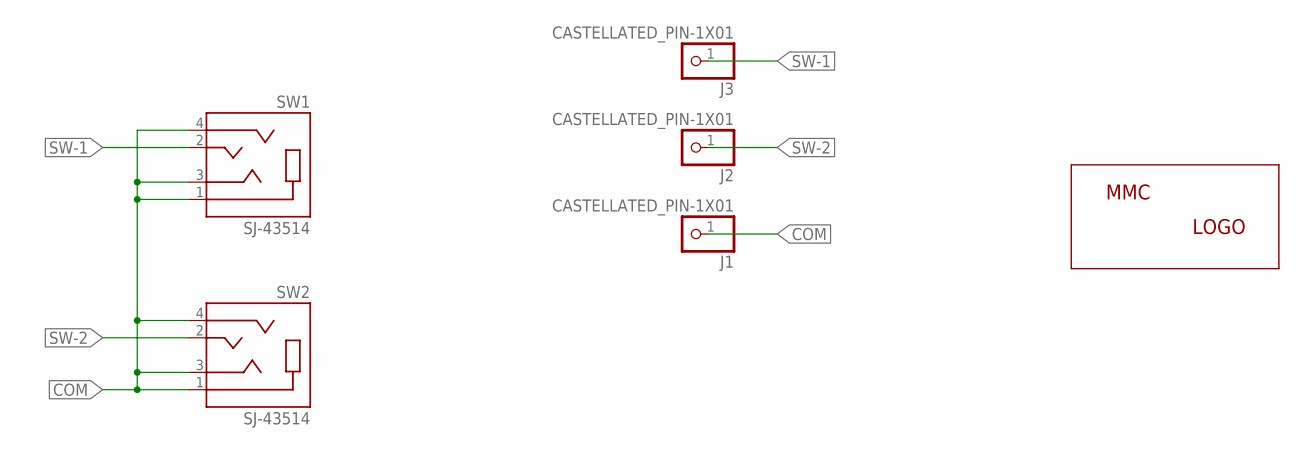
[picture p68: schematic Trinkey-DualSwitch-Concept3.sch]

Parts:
J1, J2, J3: CASTELLATED_PIN-1X01
LABEL_LOGO: MMC_LOGO-XSM; MMC_X-SMALL_LOGO
SW1, SW2: SJ-43514; CUI_SJ-43514

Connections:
COM: J1.1, SW1.1 (SLEEVE), SW1.3 (RING1), SW1.4 (RING2), SW2.1 (SLEEVE), SW2.3 (RING1), SW2.4 (RING2)
SW-1: J3.1, SW1.2 (TIP)
SW-2: J2.1, SW2.2 (TIP)

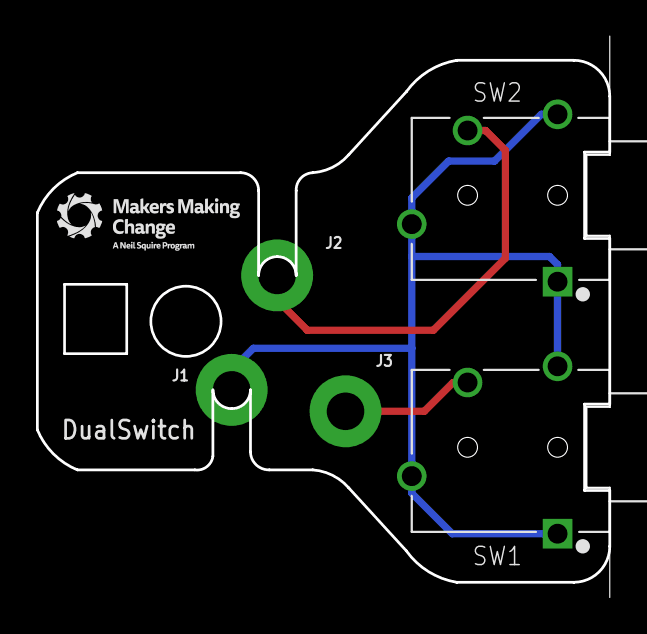
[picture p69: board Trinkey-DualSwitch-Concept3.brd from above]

Board: 2 copper layers, 31.8 x 31.2 mm, 6 parts (0 on the bottom side), 3 nets.

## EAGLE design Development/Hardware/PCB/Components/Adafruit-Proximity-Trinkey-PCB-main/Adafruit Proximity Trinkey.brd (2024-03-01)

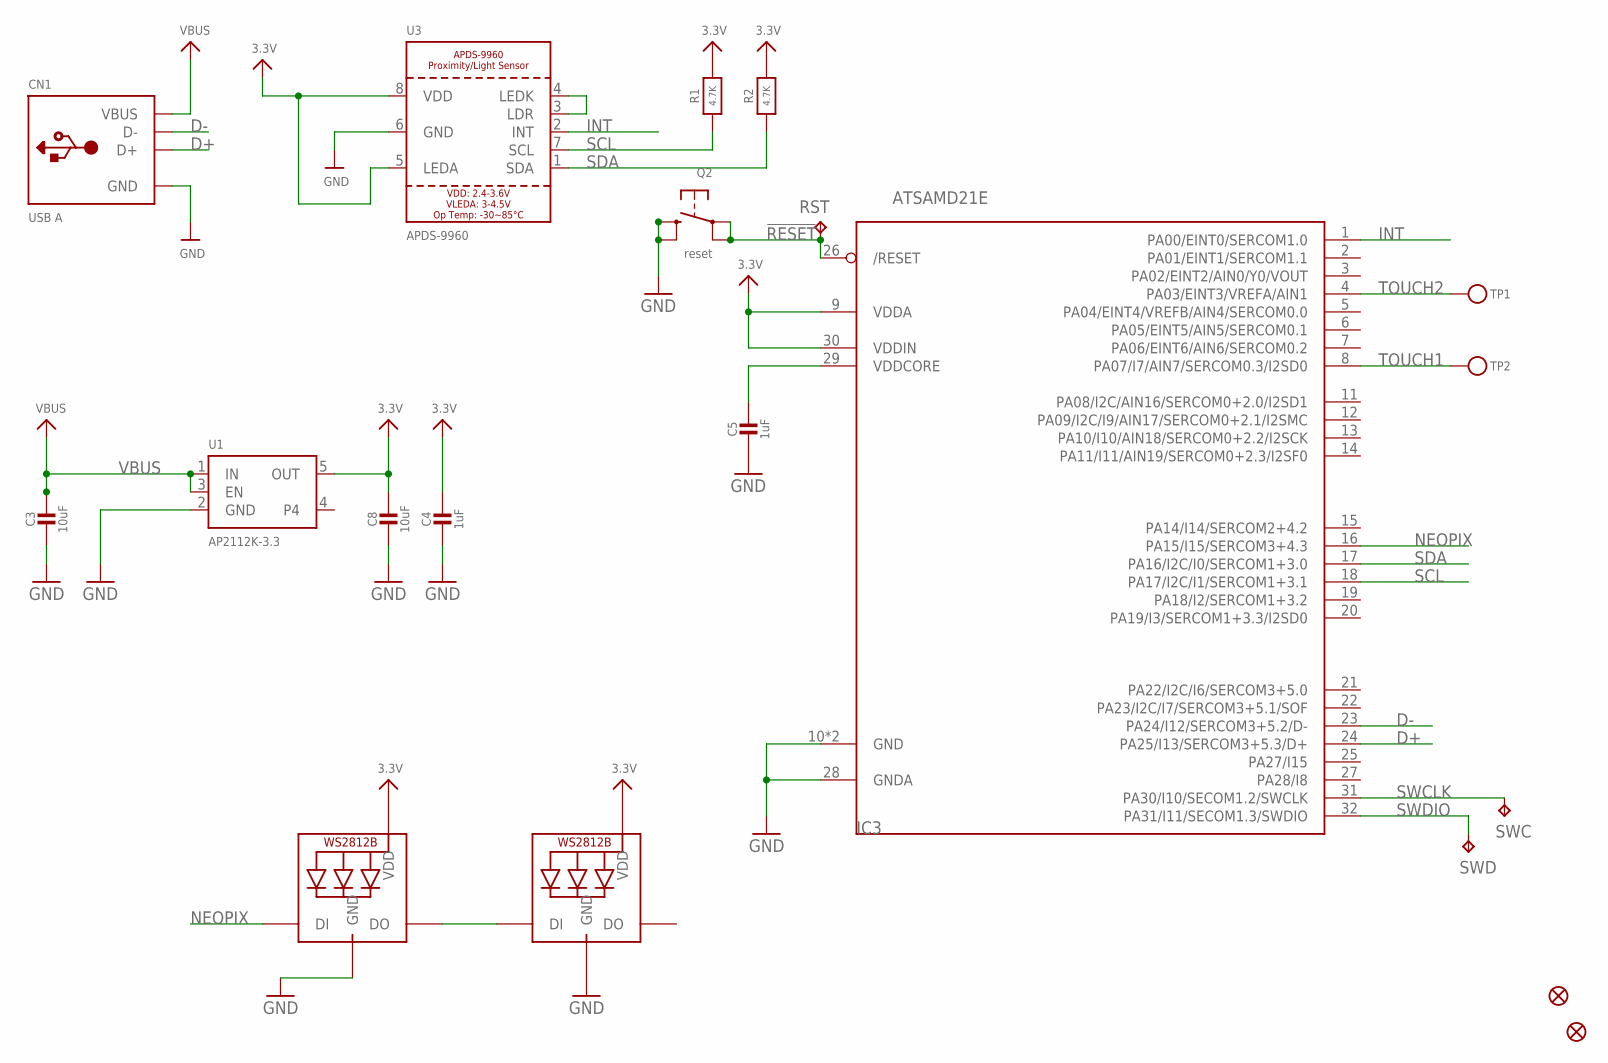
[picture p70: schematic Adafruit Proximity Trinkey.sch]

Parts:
C3, C8: 10uF; 0805-NO
C4, C5: 1uF; 0603-NO
CN1: USB A; USBA_PCB
FID1, FID2: FIDUCIAL_1MM
IC3: ATSAMD21E; QFN32_5MM
LED1, LED2: WS2812B3535; LED3535
Q2: reset; BTN_KMR2_4.6X2.8
R1, R2: 4.7K; 0603-NO
RST: TPTP16R; TP16R
SWC: TPTP15R; TP15R
SWD: TPTP16R; TP16R
TP1, TP2: TESTPOINTROUND1.5MMNO; TESTPOINT_ROUND_1.5MM_NO
U1: AP2112K-3.3; SOT23-5
U3: APDS-9960

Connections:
3.3V: C4.1, C8.1, IC3.9 (VDDA), IC3.30 (VDDIN), LED1.2 (VDD), LED2.2 (VDD), R1.2, R2.2, U1.5 (OUT), U3.5 (LEDA), U3.8 (VDD)
!RESET: IC3.26 (/RESET), Q2.A, Q2.A' (P1), RST.TP
D+: CN1.USB_PLUS (D+), IC3.24 (PA25/I13/SERCOM3+5.3/D+)
D-: CN1.USB_NEG (D-), IC3.23 (PA24/I12/SERCOM3+5.2/D-)
GND: C3.2, C4.2, C5.2, C8.2, CN1.GND, IC3.10 (GND), IC3.28 (GNDA), IC3.33 (GND), LED1.4 (GND), LED2.4 (GND), Q2.B (S), Q2.B' (S1), U1.2 (GND), U3.6 (GND)
INT: IC3.1 (PA00/EINT0/SERCOM1.0), U3.2 (INT)
unnamed: LED1.1 (DI), LED2.3 (DO)
unnamed: U3.3 (LDR), U3.4 (LEDK)
NEOPIX: IC3.16 (PA15/I15/SERCOM3+4.3), LED2.1 (DI)
SCL: IC3.18 (PA17/I2C/I1/SERCOM1+3.1), R1.1, U3.7 (SCL)
SDA: IC3.17 (PA16/I2C/I0/SERCOM1+3.0), R2.1, U3.1 (SDA)
SWCLK: IC3.31 (PA30/I10/SECOM1.2/SWCLK), SWC.TP
SWDIO: IC3.32 (PA31/I11/SECOM1.3/SWDIO), SWD.TP
TOUCH1: IC3.8 (PA07/I7/AIN7/SERCOM0.3/I2SD0), TP2.P$1
TOUCH2: IC3.4 (PA03/EINT3/VREFA/AIN1), TP1.P$1
VBUS: C3.1, CN1.VCC (VBUS), U1.1 (IN), U1.3 (EN)
VDDCORE1: C5.1, IC3.29 (VDDCORE)

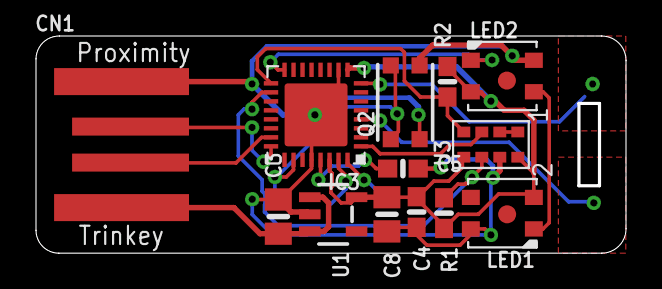
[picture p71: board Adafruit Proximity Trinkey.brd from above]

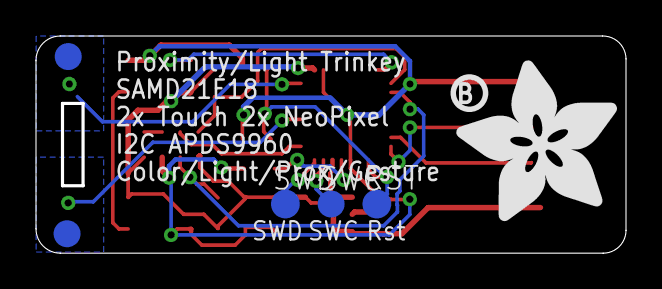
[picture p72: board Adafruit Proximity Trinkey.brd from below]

Board: 2 copper layers, 32.8 x 12.1 mm, 22 parts (7 on the bottom side), 17 nets.

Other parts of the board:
U$8: PCBFEAT-REV-040
U$10: ADAFRUIT_9MM

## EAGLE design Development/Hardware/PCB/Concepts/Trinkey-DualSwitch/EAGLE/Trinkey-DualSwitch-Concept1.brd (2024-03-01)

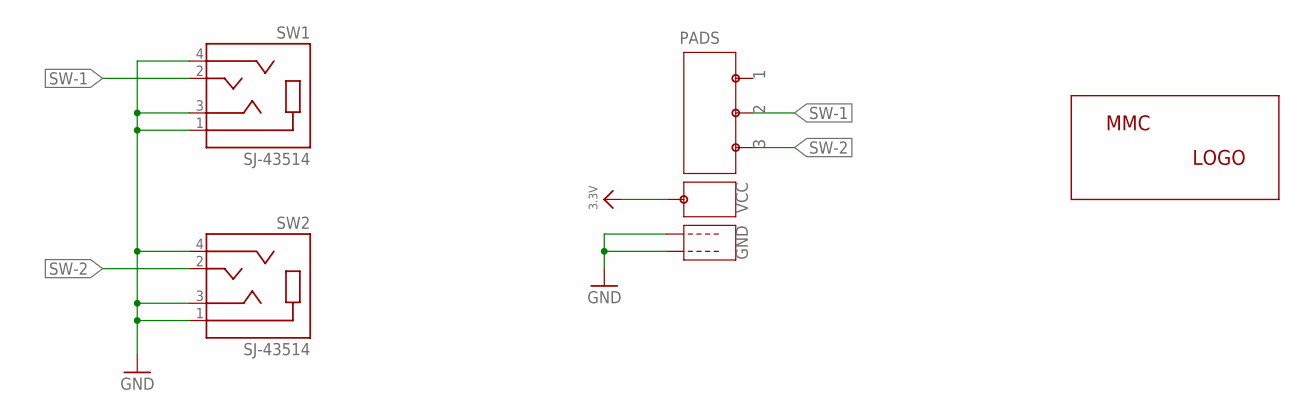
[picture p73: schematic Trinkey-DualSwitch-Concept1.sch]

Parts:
LABEL_LOGO: MMC_LOGO-XSM; MMC_X-SMALL_LOGO
PADS: CASTELLATED-ROTARY-TRINKEY
SW1, SW2: SJ-43514; CUI_SJ-43514

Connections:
3.3V: PADS.P$VCC
GND: PADS.P$GND1, PADS.P$GND2, SW1.1 (SLEEVE), SW1.3 (RING1), SW1.4 (RING2), SW2.1 (SLEEVE), SW2.3 (RING1), SW2.4 (RING2)
SW-1: PADS.P$S2, SW1.2 (TIP)
SW-2: PADS.P$S3, SW2.2 (TIP)

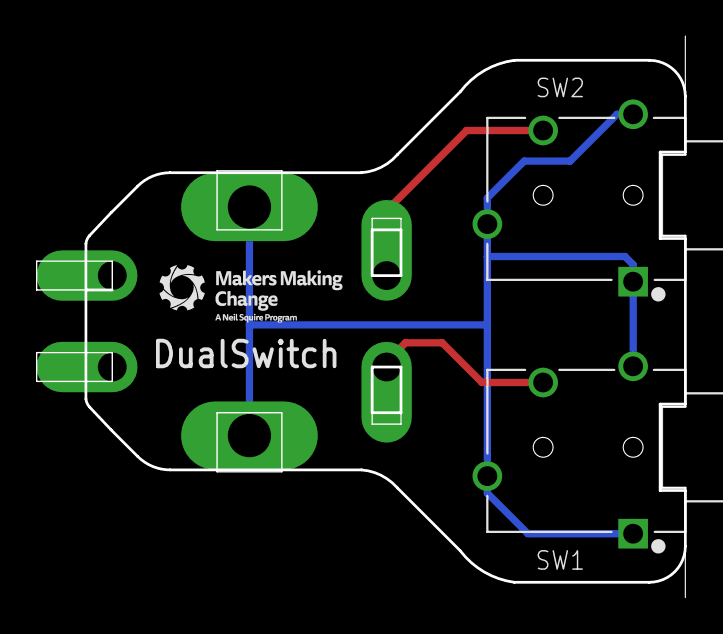
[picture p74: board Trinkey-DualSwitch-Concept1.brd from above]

Board: 2 copper layers, 36.0 x 31.2 mm, 4 parts (1 on the bottom side), 3 nets.

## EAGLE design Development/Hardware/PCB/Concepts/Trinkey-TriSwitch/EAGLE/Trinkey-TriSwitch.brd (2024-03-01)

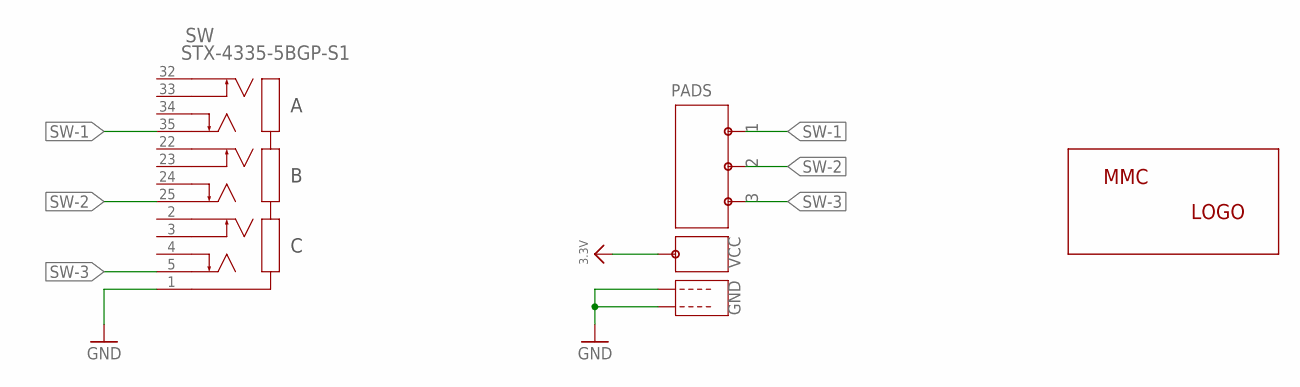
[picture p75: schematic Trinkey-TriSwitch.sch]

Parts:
LABEL_LOGO: MMC_LOGO-XSM; MMC_X-SMALL_LOGO
PADS: CASTELLATED-ROTARY-TRINKEY
SW: STX-4335-5BGP-S1; STX-4335-5BGP-S1_KYC

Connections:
3.3V: PADS.P$VCC
GND: PADS.P$GND1, PADS.P$GND2, SW.1
SW-1: PADS.P$S1, SW.35
SW-2: PADS.P$S2, SW.25
SW-3: PADS.P$S3, SW.5


Board: 2 copper layers, 43.7 x 16.7 mm, 3 parts (1 on the bottom side), 4 nets.

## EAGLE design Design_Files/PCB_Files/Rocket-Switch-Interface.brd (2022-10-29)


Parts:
H1: MOUNT-HOLE-3MM-CLEAR; HOLE-3MM-CLEAR
LABEL_BACKGROUND: MMC_ICON-ROCKET-SW; ICON_ROCKET-SWITCH
LABEL_DEVICE: MMC_LABEL-ROCKET-SW; LABEL-ROCKET-SWITCH
LABEL_LOGO: MMC_LOGO-XSM; MMC_X-SMALL_LOGO
PADS: PADS-ROTARY-TRINKEY-3
R1, R2: 4.7K; RESISTOR_0204/5
SW1, SW2: SJ-43514; CUI_SJ-43514

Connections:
3.3V: PADS.P$VCC, R1.2, R2.2
GND: PADS.P$GND1, PADS.P$GND2, SW1.1 (SLEEVE), SW1.3 (RING1), SW1.4 (RING2), SW2.1 (SLEEVE), SW2.3 (RING1), SW2.4 (RING2)
SW-1: PADS.P$ROT2, R1.1, SW1.2 (TIP)
SW-2: PADS.P$SW, R2.1, SW2.2 (TIP)

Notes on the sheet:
By: Milad Hajihassan
MakersMakingChange.Com


Board: 2 copper layers, 36.4 x 28.0 mm, 9 parts (1 on the bottom side), 4 nets.

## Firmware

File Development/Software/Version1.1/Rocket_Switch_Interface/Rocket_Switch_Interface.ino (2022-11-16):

/** ************************************************************************
 * File Name: Rocket_Switch_Interface.ino 
 * Title: Rocket Switch Interface
 * Developed by: MakersMakingChange
 * Version Number: 1.1 (15/11/2022)
 * Github Link: https://github.com/makersmakingchange/Rocket-Switch-Interface
 ***************************************************************************/

#include "Mouse.h"
#include "Keyboard.h"
#include <StopWatch.h>
#include <math.h>
#include <Adafruit_NeoPixel.h>
#include <FlashStorage.h>


//Can be changed based on the needs of the users
#define MOUSE_MOVE_MULTI         2                                        //Morse mouse move multiplier 
#define SWITCH_REACTION_TIME     50                                       //Minimum time for each switch action ( level 10 : 1x50 =50ms , level 1 : 10x50=500ms )
#define SWITCH_MODE_CHANGE_TIME  4000                                     //How long to hold switch 4 to change mode 

#define LED_BRIGHTNESS           150                                      //The mode led color brightness which is always on ( Use a low value to decrease power usage )
#define LED_ACTION_BRIGHTNESS    150                                      //The action led color brightness which can be a higher value than LED_BRIGHTNESS


//Define Switch pins
#define LED_PIN                  0
#define SWITCH1_PIN              2
#define SWITCH2_PIN              3

// Variable Declaration

//Declare switch state variables for each switch
int switch1State;
int switch2State;


//Stopwatches array used to time switch presses
StopWatch timeWatcher[3];
StopWatch switch2TimeWatcher[1];

//Declare Switch variables for settings 
int switchConfigured;
int switchReactionTime;
int switchReactionLevel;
int switchMouseMove;
int switchMode;

int morseReactionTime;

FlashStorage(switchConfiguredFlash, int);
FlashStorage(switchReactionLevelFlash, int);
FlashStorage(switchModeFlash, int);
FlashStorage(switchswitchMouseMoveFlash, int);

char inputCommand[7];

//RGB LED Color code structure 

struct rgbColorCode {
    int r;    // red value 0 to 255
    int g;   // green value
    int b;   // blue value
 };

//Color structure 
typedef struct { 
  uint8_t colorNumber;
  String colorName;
  rgbColorCode colorCode;
} colorStruct;

 //Mode structure 
typedef struct { 
  uint8_t modeNumber;
  String modeName;
  uint8_t modeColorNumber;
} modeStruct;


 //Switch structure 
typedef struct { 
  uint8_t switchNumber;
  uint8_t switchChar;
  uint8_t switchMacChar;
  uint8_t switchMouseAction;
  uint8_t switchColorNumber;
} switchStruct;


 //Settings Action structure 
typedef struct { 
  uint8_t settingsActionNumber;
  String settingsActionName;
  uint8_t settingsActionColorNumber;
} settingsActionStruct;

//Color properties 
const colorStruct colorProperty[] {
    {1,"Green",{60,0,0}},
    {2,"Pink",{0,50,60}},
    {3,"Yellow",{60,50,0}},    
    {4,"Orange",{20,60,0}},
    {5,"Blue",{0,0,60}},
    {6,"Red",{0,60,0}},
    {7,"Purple",{0,50,128}},
    {8,"Teal",{128,0,128}}       
};



//Switch properties 
const switchStruct switchProperty[] {
    {1,'a', KEY_F1, 5, 6},                             //{1=dot,'a',  KEY_F1, mouse action 5, 6=red}
    {2,'b', KEY_F2, 6, 5}                              //{2=dash,'b',KEY_F2, mouse action 6, 5=blue}
};



//Settings Action properties 
const settingsActionStruct settingsProperty[] {
    {1,"Decrease Reaction",6},                             //{1=Increase Reaction,5=blue}
    {2,"Increase Reaction",5},                             //{2=Decrease Reaction,6=red}
    {3,"Max Reaction",3},                                  //{3=Max Reaction,1=yellow}
    {4,"Min Reaction",3},                                  //{4=Min Reaction,1=yellow}
    {5,"Web Update",1}                                     //{5,"Web Update",2=green}
};

//Mode properties 
const modeStruct modeProperty[] {
    {1,"Switch",8},
    {2,"Switch Mac",2},
    {3,"Mouse Switch",7},
    {4,"Settings",4}
};


//Setup NeoPixel LED
Adafruit_NeoPixel ledPixels = Adafruit_NeoPixel(1, LED_PIN, NEO_GRB + NEO_KHZ800);

void setup() {

  ledPixels.begin();                                                           //Start NeoPixel
  Serial.begin(115200);                                                        //Start Serial
  Keyboard.begin();                                                            //Starts keyboard emulation
  Mouse.begin();                                                               //Starts mouse emulation
  delay(1000);
  switchSetup();                                                               //Setup switch
  delay(5); 
  displayFeatureList();
  delay(5);
  initLedFeedback();                                                          //Led will blink in a color to show the current mode 


  //Initialize the LED pin as an output
  pinMode(LED_PIN, OUTPUT);                 
  //Initialize the switch pins as an input                                     
  pinMode(SWITCH1_PIN, INPUT_PULLUP);
  pinMode(SWITCH2_PIN, INPUT_PULLUP);
};

void loop() {

  static int ctr;                          //Control variable to set previous status of switches 
  unsigned long timePressed;               //Time that switch one or two are pressed
  unsigned long timeNotPressed;            //Time that switch one or two are not pressed
  static int previousSwitch2State;         //Previous status of switch 2
  
  //Update status of switch inputs
  switch1State = digitalRead(SWITCH1_PIN);
  switch2State = digitalRead(SWITCH2_PIN);

  timePressed = timeNotPressed  = 0;       //reset time counters
  if (!ctr) {                              //Set previous status of switch two 
    previousSwitch2State = HIGH;  
    ctr++;
  }
  //Check if switch 2 is pressed to change switch mode
  if (switch2State == LOW && previousSwitch2State == HIGH) {
     if (switch2State == LOW) { 
      previousSwitch2State = LOW; 
     }
     switch2TimeWatcher[0].stop();                                //Reset and start the timer         
     switch2TimeWatcher[0].reset();                                                                        
     switch2TimeWatcher[0].start(); 
  }
  // Switch 2 was released
  if (switch2State == HIGH && previousSwitch2State == LOW) {
    previousSwitch2State = HIGH;
    timePressed = switch2TimeWatcher[0].elapsed();                //Calculate the time that switch one was pressed 
    switch2TimeWatcher[0].stop();                                 //Stop the single action (dot/dash) timer and reset
    switch2TimeWatcher[0].reset();
    //Perform action if the switch has been hold active for specified time
    if (timePressed >= SWITCH_MODE_CHANGE_TIME){
      incrementSwitchMode();                                                                
    } else if(switchMode==4) {
      settingsAction(switch1State,LOW); 
    }
  }
  //Perform actions based on the mode
  switch (switchMode) {
      case 1:
        keyboardAction(false,switch1State,switch2State);                                    //Keyboard Switch mode
        break;
      case 2:
        keyboardAction(true,switch1State,switch2State);                                     //Mac Keyboard Switch mode
        break;
      case 3:
        mouseAction(switch1State,switch2State);                                             //Mouse Switch mode
        break;
      case 4:
        settingsAction(switch1State,HIGH);                                                  //Settings mode
        break;
  };
  ledPixels.show(); 
  delay(5);
}

//***DISPLAY FEATURE LIST FUNCTION***//

void displayFeatureList(void) {

  Serial.println(" ");
  Serial.println(" --- ");
  Serial.println("Rocket Switch Interface");
  Serial.println(" ");
  Serial.println("VERSION: 1.0 (5 October 2022)");
  Serial.println(" --- ");
  Serial.println(" ");

}

//***MODIFY SETTINGS FUNCTION***//

void modifySetting(void) {
  if (Serial.available() > 0) {
    String serialString = Serial.readString();
    if(serialString.length()==6){
      String outputString = "";
      serialString.toCharArray(inputCommand, 7);
      if(inputCommand[0] == 'S' && inputCommand[1] == 'S' && inputCommand[2] == ',' && inputCommand[3] == '0' && inputCommand[4] == ':' && inputCommand[5] == '0'){
        inputCommand[5] = switchReactionLevel;
        outputString = String(inputCommand);
        Serial.println(outputString);
      }
      else if(inputCommand[0] == 'S' && inputCommand[1] == 'S' && inputCommand[2] == ',' && inputCommand[3] == '1' && inputCommand[4] == ':'){
        updateReactionLevel(inputCommand[5]-'0');
        inputCommand[5] = switchReactionLevel;
        outputString = String(inputCommand);
        Serial.println(outputString);
      }
      else if(inputCommand[0] == 'M' && inputCommand[1] == 'D' && inputCommand[2] == ',' && inputCommand[3] == '0' && inputCommand[4] == ':' && inputCommand[5] == '0'){
        inputCommand[5] = switchMode;
        outputString = String(inputCommand);
        Serial.println(outputString);
      }
      else if(inputCommand[0] == 'M' && inputCommand[1] == 'D' && inputCommand[2] == ',' && inputCommand[3] == '1' && inputCommand[4] == ':'){
        updateSwitchMode(inputCommand[5]-'0');
        inputCommand[5] = switchMode;
        outputString = String(inputCommand);
        Serial.println(outputString);
      }
    }

  }
}



//***RGB LED FUNCTION***//

void setLedBlink(int numBlinks, int delayBlinks, int ledColor,uint8_t ledBrightness) {
  if (numBlinks < 0) numBlinks *= -1;

      for (int i = 0; i < numBlinks; i++) {
        ledPixels.setPixelColor(0, ledPixels.Color(colorProperty[ledColor-1].colorCode.g,colorProperty[ledColor-1].colorCode.r,colorProperty[ledColor-1].colorCode.b));
        ledPixels.setBrightness(ledBrightness);
        ledPixels.show(); 
        delay(delayBlinks);
        ledPixels.setPixelColor(0, ledPixels.Color(0,0,0));
        ledPixels.setBrightness(ledBrightness);
        ledPixels.show(); 
        delay(delayBlinks);
      }
}

//***UPDATE RGB LED COLOR FUNCTION***//

void updateLedColor(int ledColor, uint8_t ledBrightness) {
    ledPixels.setPixelColor(0, ledPixels.Color(colorProperty[ledColor-1].colorCode.g,colorProperty[ledColor-1].colorCode.r,colorProperty[ledColor-1].colorCode.b));
    ledPixels.setBrightness(ledBrightness);
    ledPixels.show();
}

//***GET RGB LED COLOR FUNCTION***//

uint32_t getLedColor(int ledModeNumber) {

  int colorNumber= modeProperty[ledModeNumber-1].modeColorNumber-1;
  
  return (ledPixels.Color(colorProperty[colorNumber].colorCode.g,colorProperty[colorNumber].colorCode.r,colorProperty[colorNumber].colorCode.b));
}

//***GET RGB LED BRIGHTNESS FUNCTION***//

uint8_t getLedBrightness() {
  return (ledPixels.getBrightness());
}

//***SET RGB LED COLOR FUNCTION***//

void setLedColor (uint32_t ledColor, uint8_t ledBrightness){
  ledPixels.setPixelColor(0, ledColor);
  ledPixels.setBrightness(ledBrightness);
  ledPixels.show(); 
}

//***SET RGB LED BRIGHTNESS FUNCTION***//

void setLedBrightness(uint8_t ledBrightness) {
  ledPixels.setBrightness(ledBrightness);
  ledPixels.show();
}

//***CLEAR RGB LED FUNCTION***//

void ledClear() {
  ledPixels.setPixelColor(0, ledPixels.Color(0,0,0));
  ledPixels.show(); 
}

void switchFeedback(int switchNumber,int modeNumber,int delayTime, int blinkNumber =1)
{
  //Get previous led color and brightness 
  uint32_t previousColor = getLedColor(modeNumber);
  uint8_t previousBrightness = getLedBrightness();
 
  //updateLedColor(switchProperty[switchNumber-1].switchColorNumber,LED_ACTION_BRIGHTNESS);
  //delay(MORSE_REACTION);
  setLedBlink(blinkNumber,delayTime,switchProperty[switchNumber-1].switchColorNumber,LED_ACTION_BRIGHTNESS);
  delay(5);

  //Set previous led color and brightness 
  setLedColor(previousColor,previousBrightness);
  
}
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

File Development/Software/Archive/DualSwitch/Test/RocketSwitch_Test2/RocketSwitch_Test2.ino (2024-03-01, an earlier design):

#include <Adafruit_NeoPixel.h>
#define PIN_NEOPIXEL 0

const int switchPin1 = 2;     
const int switchPin2 = 3;    

// variables will change:
int switch1State = 0; 
int switch2State = 0; 

// Create the neopixel strip with the built in definitions NUM_NEOPIXEL and PIN_NEOPIXEL
Adafruit_NeoPixel strip = Adafruit_NeoPixel(1, PIN_NEOPIXEL, NEO_GRB + NEO_KHZ800);
int16_t neo_brightness = 50; // initialize with 50 brightness (out of 255)

void setup() {

  Serial.begin(115200);  
  // initialize the LED pin as an output:
  pinMode(switchPin1, INPUT_PULLUP);
  pinMode(switchPin2, INPUT_PULLUP);

  strip.begin();
  strip.setBrightness(neo_brightness);
  strip.show(); // Initialize all pixels to 'off'
}

void loop() {
  // read the state of the pushbutton value:
  switch1State = digitalRead(switchPin1);
  switch2State = digitalRead(switchPin2);

  // check if the pushbutton is pressed. If it is, the buttonState is HIGH:
  if (switch1State == LOW) {
    Serial.println("Switch 1 is pressed");
    strip.setBrightness(neo_brightness);
    strip.setPixelColor(0, 255, 0, 255);
    strip.show();
  } 
  if (switch2State == LOW) {
    Serial.println("Switch 2 is pressed");
    strip.setBrightness(neo_brightness);
    strip.setPixelColor(0, 255, 255, 0);
    strip.show();
  }
  delay(100);
  strip.setBrightness(neo_brightness);
  strip.setPixelColor(0, 0, 0, 0);
  strip.show();
  strip.clear();
}

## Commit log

2022-10-29 Added version 1.0 build, design, and documentation files
    [Rocket-Switch-Interface-Bottom-Case.stl, Rocket-Switch-Interface-Jig.f3z, Rocket-Switch-Interface-Jig.stl, Rocket-Switch-Interface-Top-Case.stl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]
2022-11-21 Pre-publishing Update
    [Adafruit NeoKey Trinkey.brd, Adafruit NeoKey Trinkey.sch, Adafruit Proximity Trinkey.brd, Adafruit Proximity Trinkey.sch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]
2023-06-01 Updated to version 1.1
    [Rocket-Switch-Interface-Bottom-Case.stl, Rocket-Switch-Interface-Jig.f3z, Rocket-Switch-Interface-Jig.stl, Rocket-Switch-Interface-Top-Case.stl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]
2025-06-06 Added guide for using with Apple mobile devices

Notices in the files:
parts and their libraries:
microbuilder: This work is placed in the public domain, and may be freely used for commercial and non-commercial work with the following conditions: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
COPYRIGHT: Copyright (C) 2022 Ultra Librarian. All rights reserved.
